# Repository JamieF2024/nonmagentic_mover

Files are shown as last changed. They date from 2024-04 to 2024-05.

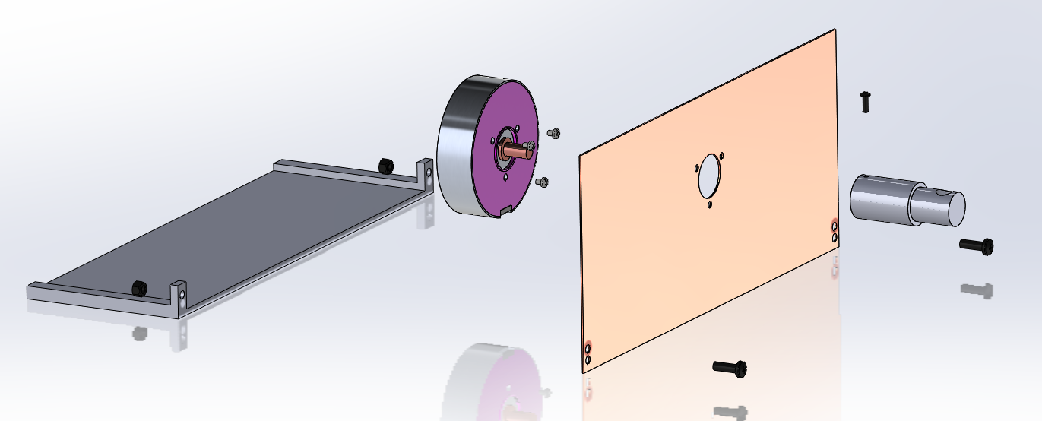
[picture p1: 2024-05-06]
SOLIDWORKS/Final Motor Assembly.png

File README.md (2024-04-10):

# nonmagentic_mover
<h1>MRI Compatible Motion Platform</h1>

Our team is working on developing an advanced MRI-compatible device that is capable of positioning a phantom and replicating physiological movements to enhance the accuracy of qMRI evaluations.

<h2>Project Overview</h2>
Imagine a clinic where doctors can quickly and painlessly measure characteristics of tissue inside a patient, without an invasive biopsy – this is the goal of quantitative magnetic resonance imaging (MRI).

Liver disease is a major public health challenge worldwide. Excessive fat accumulation (steatosis) in the liver affects approximately 25% of the world population (i.e., over one billion people), and prevalence is increasing everywhere. If untreated, steatosis can lead to further liver damage, cirrhosis, and cancer. Thus, it would be highly impactful to have a non-invasive measuring technique like quantitative MRI to determine clinically relevant quantities like liver fat and iron concentration. Making these MRI techniques robust against respiratory and other bodily motion is important for improving their “foolproofness” and facilitating their widespread adoption for use in a wider range of patients.

The Quantitative Imaging Methods Lab (QIML) in the Department of Medical Physics and Radiology is interested in the development of these motion-robust quantitative MRI methods. A motion platform which is safe for use in the highly magnetized environment of the MRI scanner, and can produce consistent motion patterns which mimic that of patients, would contribute greatly to the development and testing process for motion-robust MRI methods.

The development of a mechanical device which is MR-compatible poses some unique challenges. Magnetic metals must not be used at all, and the use of other metals (eg. brass, aluminum) should still be minimized due to the possibility of induced currents as the magnetic field varies over the course of operation of the MRI scanner. A nonmagnetic piezoelectric ultrasonic motor is available for students to integrate into their design, as well as nonmetallic linear sliding rails and bearings. Depending on the interests of the students, the project could be extended to creating motion with multiple degrees of freedom (2D planar motion or translational motion and compressive deformation) or the implementation of a MR-compatible form of closed-loop feedback.

<h2>Project Contributors </h2>
Team Members: Maxwell Naslund, Caspar Uy, Kendra Besser, Jamie Flogel, Amber Schneider 
<br></br>
Advisor: Dr. James Trevathan
<br></br>
Client: Mr. Jiayi Tang

<h2>Team Photo </h2>

Team Photo 

This project is affiliated with the University of Wisconsin-Madison, Department of Biomedical Engineering.

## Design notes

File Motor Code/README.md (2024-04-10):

<h1>Motor Code Overview</h1>
The motor assembly utilizes a WLG-75-R piezoelectric motor to generate rotational motion. This motor is controlled by a WLG-75-R-AMAG and Nucleo Board F446RE. The motor code is written in C++. It can be edited, uploaded, and run through <a href="https://studio.keil.arm.com/">Keil Studio Cloud - Arm</a>. Below are instructions for how to set up and run the main.cpp files in this folder.
<h2>Setup</h2>
<ol>
  <li>Login or Create an Account with Keil Studio Cloud.</li>
  <li>In the top right, go to File -> New -> Mbed Project.</li>
  <li>For the "Example project" field, select "empty Mbed OS project". Edit the project name to something memorable. The project should now appear as <b>active</b> in the left panel.</li>
  <li>Right click on the project name in the left panel and select Add Mbed Library.</li>
  <li> For the "URL" field, use <a href=http://os.mbed.com/users/aberk/code/QEI/>http://os.mbed.com/users/aberk/code/QEI/</a>. The Library Name field should auto-populate as "QEI". </li>
  <li>Click Next. For the "Release, Branch, or Tag" field, select "default". Click Finish. There should now be a subfolder labeled QEI. This folder contains 2 files: QEI.cpp & QEI.h.</li>
  <li>Replace the current QEI.cpp and QEI.h files in Keil Studio Cloud with the files in the GitHub Motor Code folder. You can do this by either downloading then uloading the files, or by copying and pasting their contents.</li>
  <li>Do the same for the main.cpp file found in Keil Studio Cloud and this GitHub folder.</li>
<i>Note: the main.cpp file is currently not uploaded in GitHub. Please use the Google Drive.</i>
</ol>
<b>You have now successfully finished the setup!</b>
<h2>Building & Running a Program</h2>
<i>When working in Keil Studio Cloud, make sure that the project you are working on is <b>active</b>.</i>
<ol>
  <li> Plug the Nucleo Board into the computer you are using with Keil Studio Cloud.</li>
  <li>Ensure your current project is <b>active</b>. Set the "Build target" in the left pane as "NUCLEO-F446RE".</li>
  <li>Build the project using the blue hammer button in the left pane. This will take around a minute the first time you build, but in future builds it will be quicker. Upon completion, a download should be completed as a ".bin" file.</li>
  <li> Open file explorer. Find the Nucleo Board connection under "This PC". Drag and drop the ".bin" file into the Nucleo drive.</li>
</ol>
<b>Your code is now successfully uploaded and running!</b>

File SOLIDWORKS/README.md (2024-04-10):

<h2>SOLIDWORKS Files</h2>
Many components of our design were 3D printed using PLA.
The final versions of the printed files are included in this folder.

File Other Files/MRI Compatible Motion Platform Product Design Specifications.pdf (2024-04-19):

## MRI Compatible Motion Platform - BME 400

Product Design Specifications February 27th, 2024

Client: | Mr. Jiayi Tang
Advisor: | Dr. James Trevathan
Team: | Maxwell Naslund - Team Leader Kendra Besser - Communicator Amber Schneider - BWIG Jamie Flogel - BPAG Caspar Uy - BSAC

Function

MRI phantoms are often static models of the human body that are used to test and calibrate MRI’s. Natural process’ such as respiration and digestion create constant motion within the human body. Static phantoms used to calibrate MRI’s do not properly represent this motion. This demonstrates a need for an MR compatible device that holds a phantom and is capable of simulating the movements found within the human body.

Client requirements:

- MR Compatible
- Moves back and forth
- Minimize the use of electronics inside the room
- Potentially incorporate materials currently available from the client
- Create a prototype with a budget of $1000
- Utilize commercially available parts
- Avoid complex fabrication methods

Design requirements:

### 1. Physical and Operational Characteristics

a. Performance requirements: The product will be a magnetic resonance compatible platform that provides a periodic waveform motion. The waveform motion will have a frequency of 4-20 cycles/min and amplitude of 1-6 cm to represent physiological breathing patterns. The motion will be consistent for 15 minutes and is allotted a standard deviation of 5% from the desired waveform. The product must withstand the size and weight of a phantom liver for testing purposes.
b. Safety: The device will be entirely made of MR compatible material and will pose no safety risk within the MR environment. The device’s magnetically induced displacement and torque forces will be tested to assure these forces are below their gravitational equivalents. The device will also be evaluated for RF heating, eddy currents, gradient induced vibrations, and gradient induced extrinsic electrical potential risks, as also recommended by the FDA [1]. As this device will utilize electronics, it is classified as an active medical device and will follow FDA 21 CFR part 801 and ASTM F2503 labeling requirements.
c. Accuracy and Reliability: The device must be able to produce repeatable patterns of movements within 2mm. The components of the device must not decrease the signal to noise ratio of the calibration phantom being tested. The device must be able to reliably repeat MR scans with minimal decrease in image quality between scans.
d. Life in Service: The device must operate for up to 60 minutes at a time as that is the time an MRI may take to produce an image of a medium-sized area [2]. A non-magnetic motor should last 20,000 hours under normal operating conditions [3]. Overall the device should last as long as an MRI scanner, which is approximately 10 years [4].
e. Shelf Life: Based on the motor components it should be stored in -40 to 70 °C temperatures with humidity 0 to 80% non condensing [2].
f. Operating Environment: The device must be able to withstand upwards of 3 tesla for 1 hour [5]. The device must be able to withstand potential RF heating, eddy currents, gradient induced vibrations, and gradient induced extrinsic electrical potential risks associated with devices within strong magnetic fields [1].
g. Ergonomics: The platform should have a height that is comfortable and safe for people to interact with when placed in the MRI. No force should be applied by a person to the motor or any moving parts during operation. An emergency stop feature should be implemented to allow users to immediately stop the motion platform in case of any issues or safety concerns.
h. Size: The platform will be no smaller than 25cm x 35cm in order to hold a range of phantom liver samples [6]. The platform will be rectangular shaped.
i. Weight: In order for the user to install and uninstall the platform during each segment of testing, the weight should not exceed 10kg. The platform must be able to withstand 4kg [7].

j. Materials: The product will be composed of MRI compatible materials. Ferrous and magnetic metals will not be used; other metals, such as brass and aluminum, will be limited to minimize the possibility of induced currents. A nonmagnetic ultrasonic piezoelectric motor will be used to provide platform motion. Nonmetalic sliding rails and bearings will be used to guide the platform through the MRI machine.
k. Aesthetics, Appearance, and Finish: Color, shape, form, texture of finish should be specified where possible (get opinions from as many sources as possible).

### 2. Production Characteristics

a. Quantity: Produce one motion controlled platform.
b. Target Product Cost: The budget for this project is $1000 with many of the components already provided including some motors, rails, software, and hardware. Existing MRI compatible designs cost around $9700 excluding the cost of the phantom used [7].

### 3. Miscellaneous

a. Standards and Specifications: MRI systems and accessories must follow the multiple sets of standards designed by the organizations like the FDA involving forms of testing the functionality of the machine including any additional accessories. Accessory parts should allow appropriate function in testing MRI displacement force ASTM F2052, torque ASTM F2213, RF heating ASTM F2182, and image artifact ASTM F2119 [8].
b. Customer: Preferences on stability and levelness will assist users in creating more genuine images. Reducing additional noise from both the platform and machine would be beneficial to more optimal usage.
c. Patient-related concerns: The device would need to be appropriately cleaned and disinfected for each use as instructed with the associated manufacturer. Appropriate dimensions levelness of the platform will need to be monitored to help with specimen/subject safety. Additionally cleanliness of the machine is an important consideration as the device should not leak motor oil or other fluids on the MRI bed.
d. Competition:
- Vital Biomedical Technologies MRI Compatible Multi-Modality Motion Stage is a programmable linear motion stage. This product is used in the bore of the MRI scanner and follows user-defined trajectories. The programmed trajectories are loaded onto the control system through a micro SD card. This product has a patent pending and there are a suite of other similar motion stages by this same company to address different anatomical motions [9].
- For a study done by the Department of Radiology at University of Texas Southwestern Medical Center researchers developed a one-dimensional MRI compatible motion platform. They used this in combination with an abdominal phantom to assess how movement during imaging affected the quality of images and the accuracy of quantitative metrics. This design consisted of a motorized linear stage residing inside the MRI machine and driving electronics outside the MRI room. The motorized stage followed sinusoidal, harmonic, random or user-defined trajectories. The device was used for the study and is not on the market for outside use [7].
- The Quasar MRI Motion Phantom is a completely MR safe programmable phantom. In this device the motion capable components are incorporated directly with the phantom. This design uses piezoelectric motors to create desired motions. It is intended to be used to test Deep Inspiration Breath Hold protocols. It is unclear how useful this product would be in protocols that require normal respiratory movement rather than breath holding [10].

## References

[1] “Testing and labeling medical devices for safety in the magnetic ...,” U.S. FOOD & DRUG ADMINISTRATION, https://www.fda.gov/media/74201/download?attachment (accessed Sep. 22, 2023).
[2] “How it’s performed - MRI Scan,” NHS choices, https://www.nhs.uk/conditions/mri-scan/what-happens/#:~:text=A%20magnetic%20reso nance%20imaging%20(MRI,number%20of%20images%20being%20taken. (accessed Sep. 20, 2023).
[3] “Hr4 nanomotion motor ,” NANOMOTION, https://www.nanomotion.com/product/hr4-nanomotion-motor/ (accessed Sep. 20, 2023).
[4] A. Sahu, H. Vikas, and N. Sharma, “Life cycle costing of MRI machine at a tertiary care teaching hospital,” The Indian journal of radiology &amp; imaging, https://www.ncbi.nlm.nih.gov/pmc/articles/PMC7546299/ (accessed Sep. 20, 2023).
[5] K. Albus, “Small phantom testing: MRI (revised 3-6-23),” Accreditation Support, https://accreditationsupport.acr.org/support/solutions/articles/11000061036-small-phant om-testing-mri-revised-3-6-23- (accessed Sep. 21, 2023).
[6] “Liver Phantom — The Phantom Laboratory.” https://www.phantomlab.com/liver-phantom (accessed Sep. 22, 2023).
[7] J. Nofiele et al., “An MRI-Compatible Platform for One-Dimensional Motion Management Studies in MRI,” Magnetic resonance in medicine, vol. 76, no. 2, p. 702, Aug. 2016, doi: 10.1002/mrm.25903. (https://doi.org/10.1002/mrm.25903)
[8] Center for Devices and Radiological Health. “MRI Information for Industry.” U.S. Food and Drug Administration, FDA, www.fda.gov/radiation-emitting-products/mri-magnetic-resonance-imaging/mri-informati on-industry. Accessed 20 Sept. 2023.
[9] “Motion Stages Compatible with CT, MRI, PET, SPECT & Ultrasound.” https://www.simutec.com/Products/motionstages.html (accessed Sep. 20, 2023).

[10] “QUASARTM MRI⁴D Motion Phantom,” Modus Medical Devices. https://modusqa.com/products/quasar-mri4d-motion-phantom/ (accessed Sep. 20, 2023).

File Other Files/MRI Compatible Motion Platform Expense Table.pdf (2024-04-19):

Item | Description | Manufacturer | Part Number | Date | QTY | Cost Each | Total | Link

Component 1 - Gearbox Prints

Ultimaker PLA (118 g) | 3D printed support for the driveshaft | Ultimaker | RAL-9005 | 11/17/2023 | 1 | $9.44 | $9.44 | N/A
Ultimaker PLA (126 g) | 3D printed gearbox extension pieces | Ultimaker | RAL-9005 | 2/27/2024 | 1 | $6.30 | $6.30 | N/A
Ultimaker PLA | 3D Printed Gears | Ultimaker | RAL-9005 | 3/7/2024 | 1 | $2.56 | $2.56 | N/A
Ultimaker PLA | 3D Printed Gearbox and motor stand | Ultimaker | RAL-9005 | 3/14/2024 | 1 | $19.60 | $19.60 | N/A

Component 2 - Linear Rails

Linear Rails

400 mm linear
rails | igus

CWS-06-30-4
00 | 11/13/2023 | 2 | $167.69 | $335.38 | Link (https://www.igus.com/articlerouter/?artnr=CWS-06-30-400&c=US&l=en&q_ettig=c3tYhltIigbyygX)

Component 3 - Linear Slides

Linear Slides

Slides to support
platform on linear
slides | igus

WWPL-06-30
-06 | 11/13/2023 | 2 | $18.25 | $36.50 | Link (https://www.igus.com/product?artNr=WWPL-06-30-06&q_ettig=c3tYhltIigbyygX&utm_medium=email)

Component 4 - Driveshaft

Driveshaft

Connection piece
between motor
and gearbox Grainger

H0400075PW
1000 | 11/16/2023 | 1 | $8.00 | $8.00 | Link (https://www.grainger.com/product/GF-PIPING-SYSTEMS-Pipe-PVC-5AFJ3)

Component 5 - Platform

Platform

1/4 black acrylic
sheet provided by
Makerspace MSC

MSC#
63391700 (no
part number
given similar
example) | 11/17/2023 | 1 | $20.00 | $20.00 | N/A

Component 6 - Glass Ball Bearings

Glass Ball Bearings

Glass ball
bearings to allow
for frictionless
rotation | Grainger | MSN0459939 | 12/1/2023 | 5 | $17.07 | $85.35 | N/A

Component 7 - Fastner

M5 Plastic Screws | Used to assemble final prototype | Grainger | 50M050080 H016 | 2/15/24 | 1 | $1.65 per package of 25 | $1.65 | Link (https://www.grainger.com/product/Machine-Screw-M5-Thread-Size-4DJK4)
M4 Plastic Screws | Used to assemble final prototype | Grainger | 50M040070N 035 | 2/15/24 | 2 | $5.92 per package of 25 | $11.84 | Link (https://www.grainger.com/product/Machine-Screw-M4-Thread-Size-4DFC2)

Plastic Screws and
Nuts

Plastic hardware
from the
makerspace | Makerspace | N/A | 3/6/2024 | 1 | $1.30 | $1.30 | N/A

Component 8 Power Components

Power Inverter

Power supply
inverter to
improve circuit DigiKey

PDM1-S5-D3
-S | 3/22/2024 | 2 | $5.12 | $10.24 | Link (https://www.digikey.com/en/products/detail/cui-inc/PDM1-S5-D3-S/5306611?_gl=1*1pgc32a*_up*MQ..)

Component 9 - unused features due to reprints/redesigns

Ultimaker PLA | 3D printed Gearbox | Ultimaker | RAL-9005 | 10/26/202 3 | 1 | $19.36 | $19.36 | N/A
Ultimaker PLA | Motor to driveshaft adapter piece | Ultimaker | RAL-9005 | 12/1/2023 | 1 | $1.12 | $1.12 | N/A
Ultimaker PLA | Motor to driveshaft adapter piece reprint | Ultimaker | RAL-9005 | 12/4/2023 | 1 | $2.84 | $2.84 | N/A
Ultimaker PLA | Motor to driveshaft adapter piece reprint | Ultimaker | RAL-9005 | 12/5/2024 | 1 | $2.65 | $2.65 | N/A
Ultimaker PLA (37.0 g) | 3D printed gears to translate and facilitate motion | Ultimaker | RAL-9010 | 10/26/202 3 | 1 | $2.96 | $2.96 | N/A

Ultimaker PLA (325.0 g) | 3D printed gears and gearbox | Ultimaker | RAL-9005 | 11/03/2023 | 1 | $26.00 | $26.00 | N/A
Bamboo Labs PLA (127.34 g) | 3D printed gearbox extension pieces | Bambu Lab | #000000 | 11/15/2023 | 1 | $12.19 | $12.19 | N/A
Ultimaker PLA (27 g) | 3D printed racks | Ultimaker | RAL-9005 | 11/29/2023 | 1 | $2.16 | $2.16 | N/A
Ultimaker PLA (126 g) | 3D printed Motor Stand | Ultimaker | RAL-9005 | 12/01/202 3 | 1 | $10.08 | $10.08 | N/A
Ultimaker PLA | 3D printed gears and gearbox | Ultimaker | RAL-9005 | 2/23/24 | 1 | $14.60 | $14.60 | N/A
TOTAL: | $642.12

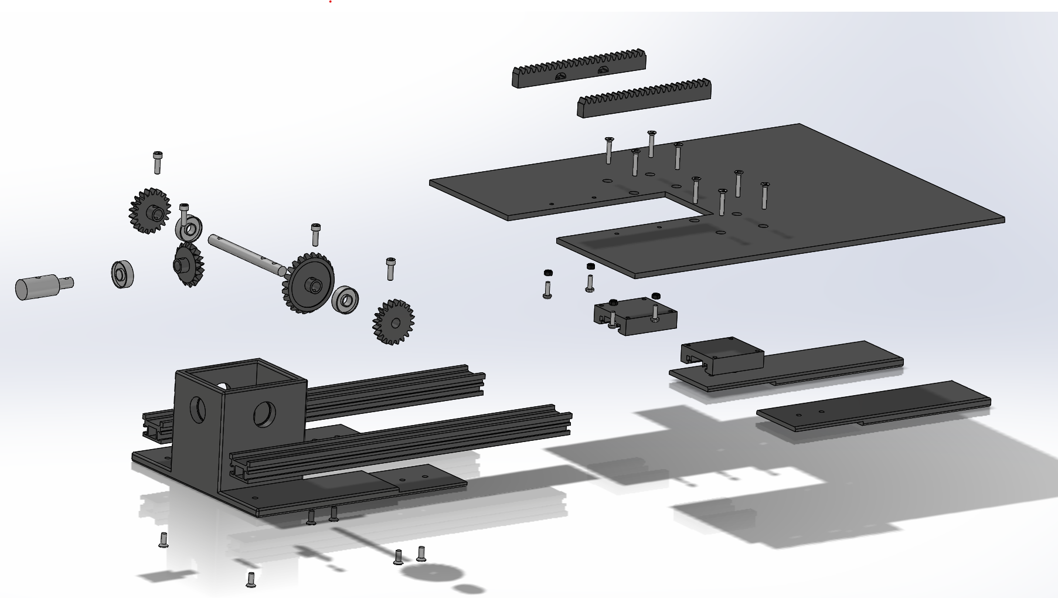
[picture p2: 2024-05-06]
SOLIDWORKS/final exploded.png

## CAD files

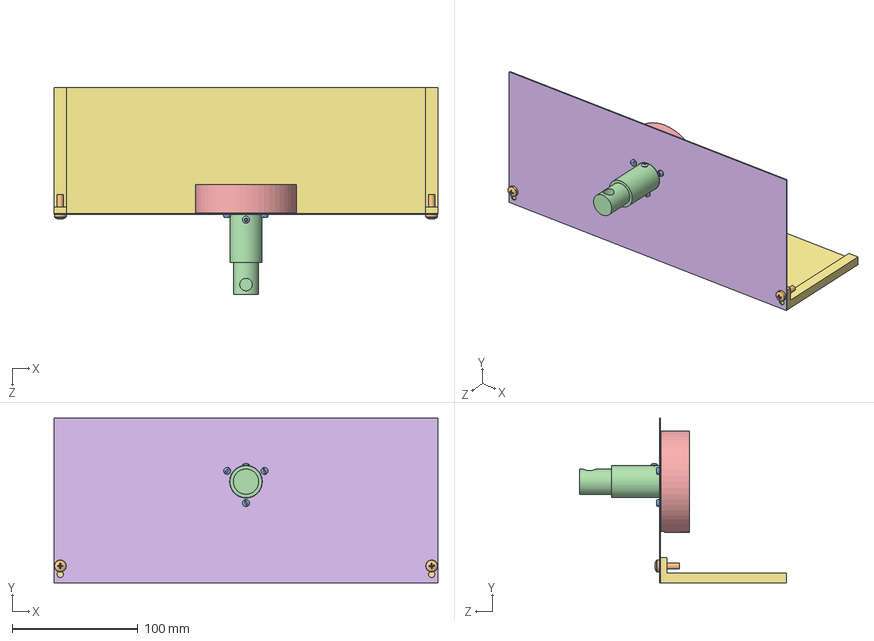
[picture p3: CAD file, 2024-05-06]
SOLIDWORKS/Final Motor Assembly.SLDASM
304.8 x 130.6 x 164.5 mm
MotorStand
MotorCopperFace
Motor
MotorDriveshaft Adaptor
Motor_M3 x 3
Stand_M5 x 2
Adaptor_M3

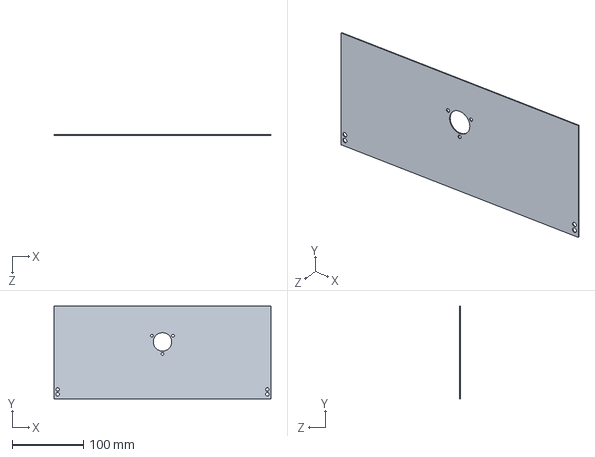
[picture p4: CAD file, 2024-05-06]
SOLIDWORKS/MotorCopperFace.SLDPRT
304.8 x 130.6 x 1.00 mm

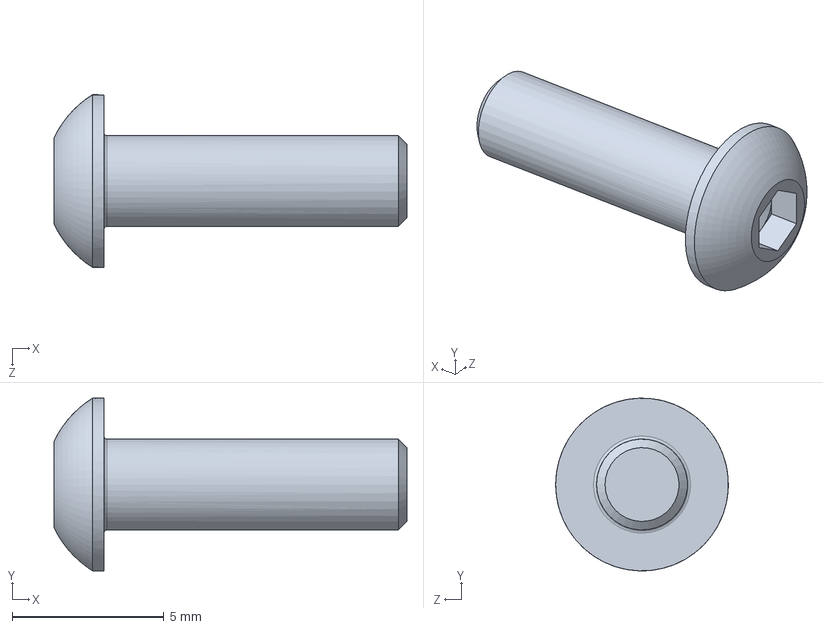
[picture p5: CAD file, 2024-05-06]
SOLIDWORKS/Adaptor_M3.SLDPRT
11.6 x 5.70 x 5.70 mm

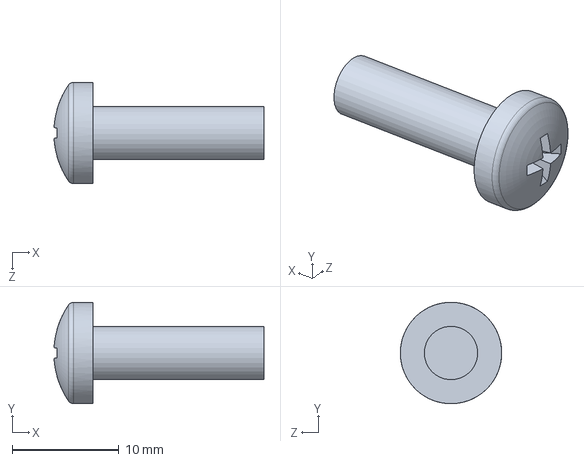
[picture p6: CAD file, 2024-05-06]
SOLIDWORKS/Stand_M5.SLDPRT
19.7 x 9.50 x 9.49 mm

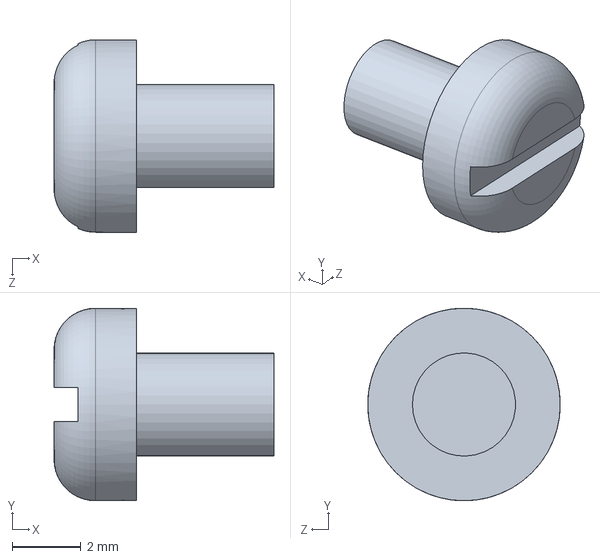
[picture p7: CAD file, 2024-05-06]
SOLIDWORKS/Motor_M3.SLDPRT
6.40 x 5.60 x 5.60 mm

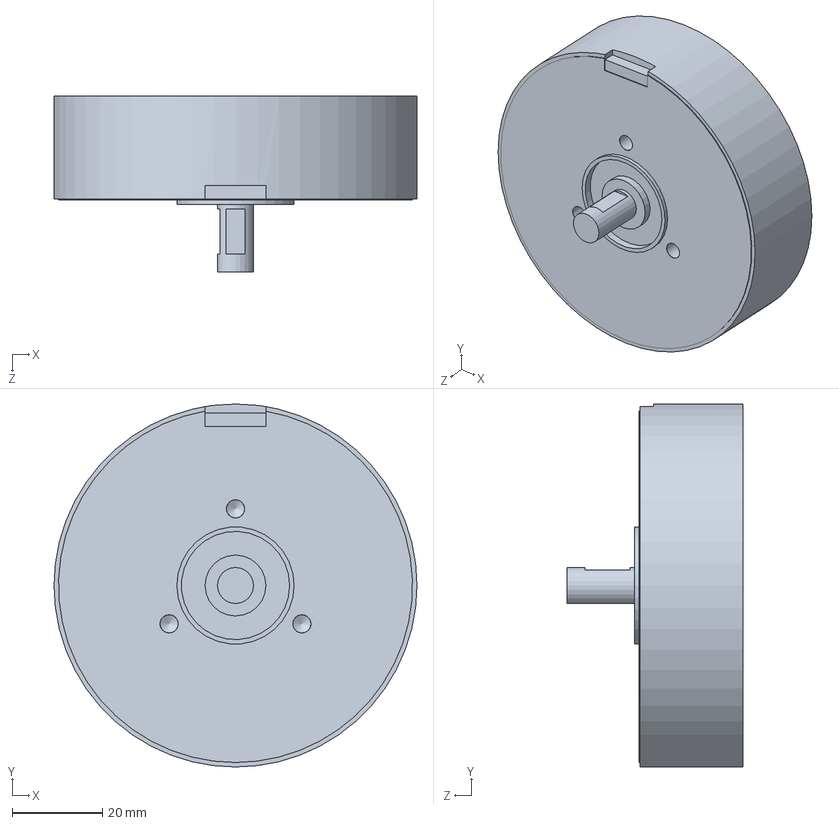
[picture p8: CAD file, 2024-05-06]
SOLIDWORKS/Motor.SLDPRT
80.5 x 80.5 x 39.0 mm

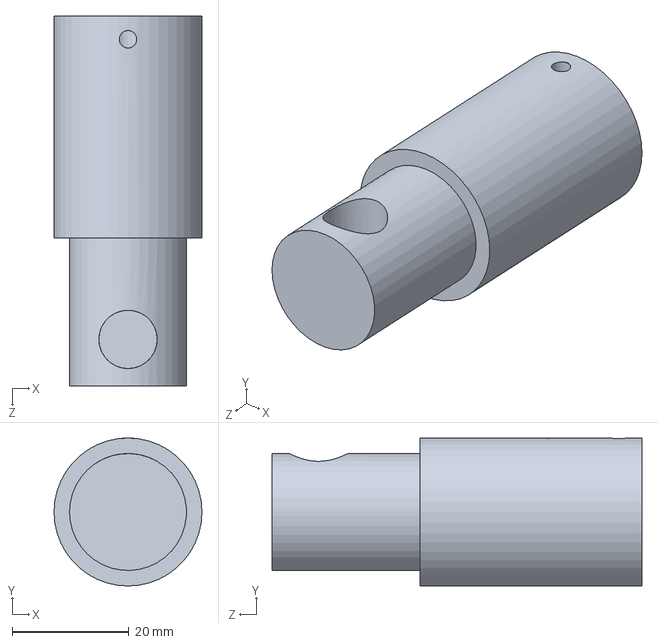
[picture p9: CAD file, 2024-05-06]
SOLIDWORKS/MotorDriveshaft Adaptor.SLDPRT
25.4 x 25.4 x 63.5 mm

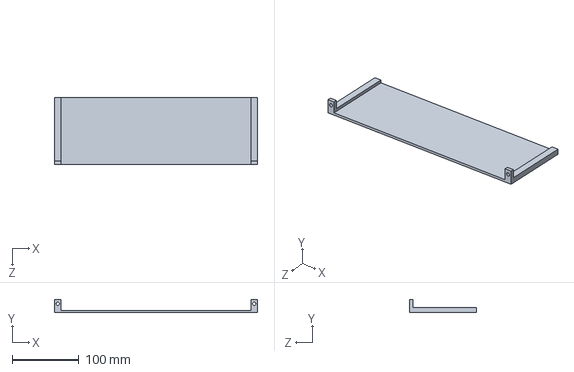
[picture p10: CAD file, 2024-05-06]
SOLIDWORKS/MotorStand.SLDPRT
304.8 x 20.0 x 100.0 mm

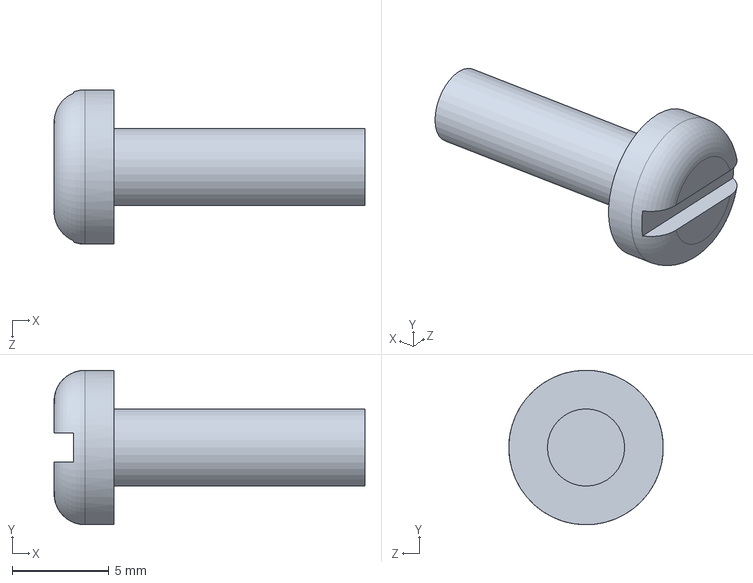
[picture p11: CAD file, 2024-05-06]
SOLIDWORKS/Rack_M4.SLDPRT
16.1 x 8.00 x 8.00 mm

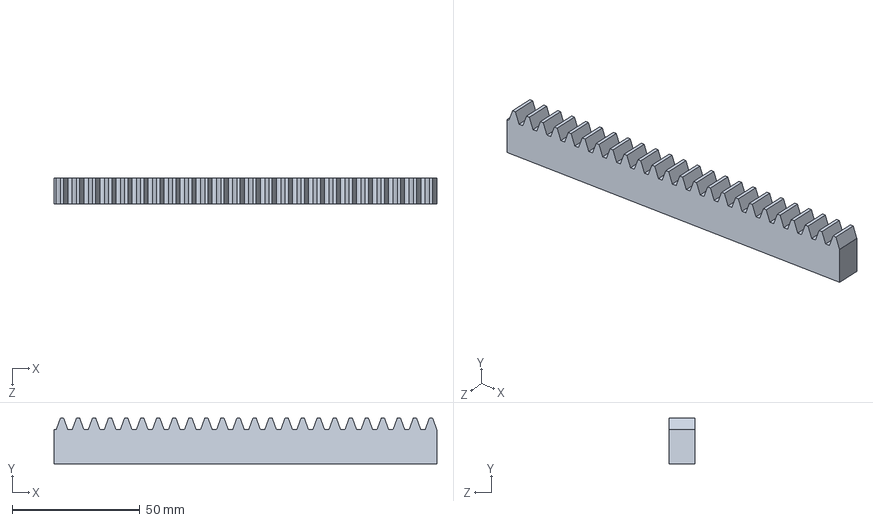
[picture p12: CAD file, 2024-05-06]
SOLIDWORKS/Rack.SLDPRT
150.0 x 18.0 x 10.0 mm

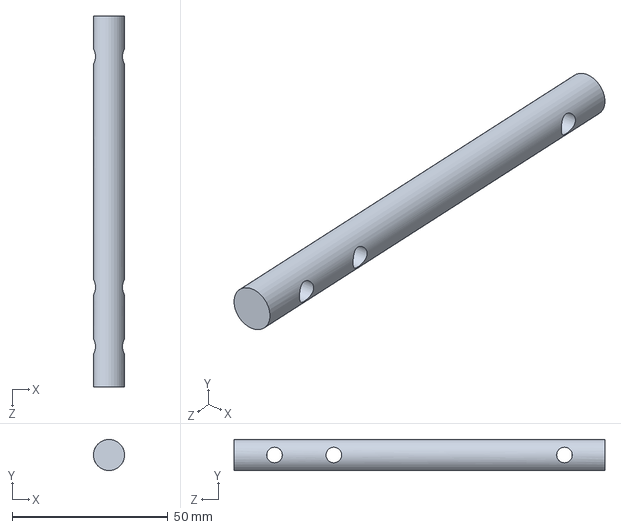
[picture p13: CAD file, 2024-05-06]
SOLIDWORKS/crosspin_new.SLDPRT
9.99 x 9.98 x 119.0 mm

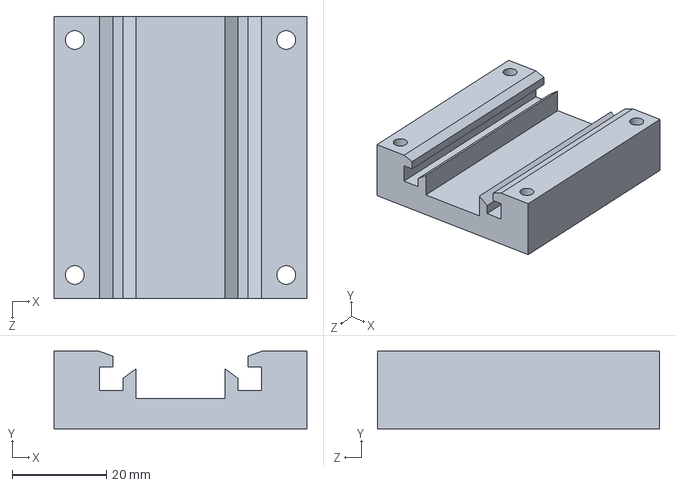
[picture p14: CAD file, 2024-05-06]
SOLIDWORKS/slide.SLDPRT
53.8 x 16.5 x 60.0 mm

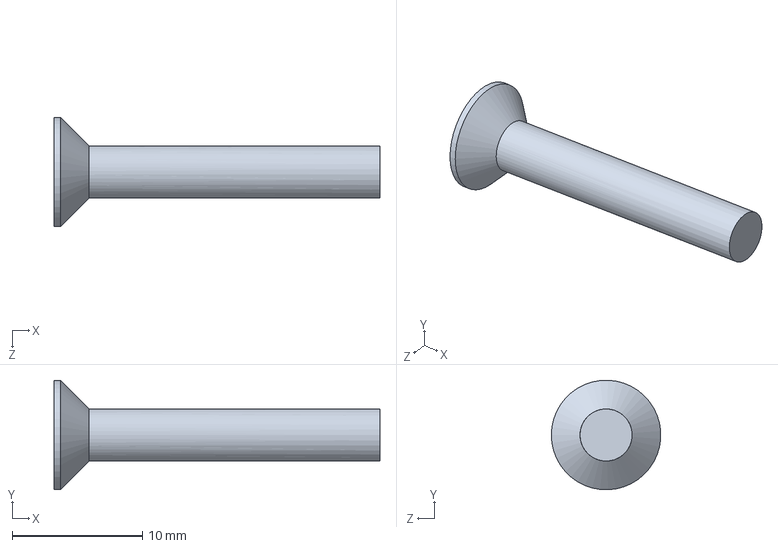
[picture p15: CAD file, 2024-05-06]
SOLIDWORKS/Slide_M4.SLDPRT
25.0 x 8.39 x 8.39 mm

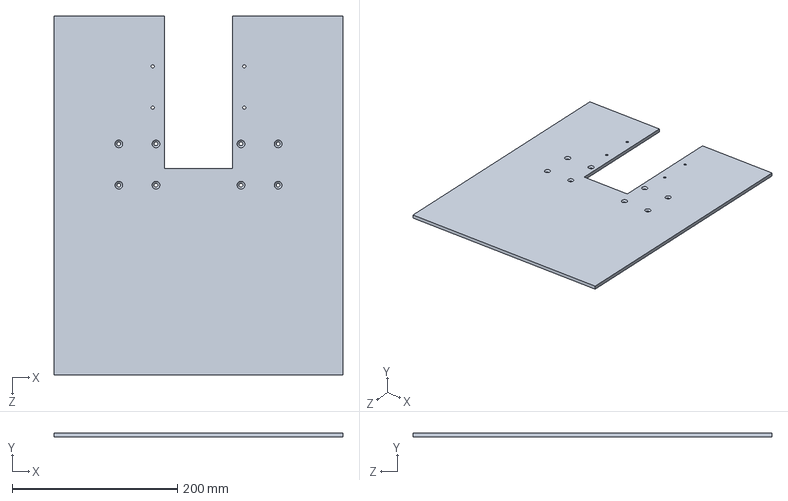
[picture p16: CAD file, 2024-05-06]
SOLIDWORKS/NewPlatform.SLDPRT
350.0 x 5.30 x 435.0 mm

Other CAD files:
SOLIDWORKS/Final Assembly.SLDASM
SOLIDWORKS/3D Printed Components.SLDASM
SOLIDWORKS/extension.SLDPRT
SOLIDWORKS/spring_gearbox.SLDPRT
SOLIDWORKS/1-1_BevelGear.SLDPRT
SOLIDWORKS/1.5-1_BevelGear.SLDPRT
SOLIDWORKS/BallBearing.SLDPRT
SOLIDWORKS/Driveshaft pin new.SLDPRT
SOLIDWORKS/Gear_M5.SLDPRT
SOLIDWORKS/Gears_M5.SLDPRT
SOLIDWORKS/M4_Nut.SLDPRT
SOLIDWORKS/MotorStand.STL
SOLIDWORKS/Rail_M5.SLDPRT
SOLIDWORKS/Stand_M5_Nut.SLDPRT
SOLIDWORKS/metric_gear.SLDPRT
SOLIDWORKS/rail.SLDPRT

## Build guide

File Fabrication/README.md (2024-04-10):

<h2>Fabrication Information</h2>
We utilized the TEAMLab at the University of Wisconsin-Madison to fabricate much of our design. This folder outlines our fabrication process.

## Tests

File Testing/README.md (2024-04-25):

<h1>Testing and Validation Information</h1>

<h2>First Round of Testing</h2>
3 tests were performed: motor encoder test, motor RPM test, and platform sinusoidal motion test.

<h3>Motor Encoder Test</h3>
This test is performed to determine if the number of revolutions counted by the motor encoder is accurate. It will reveal if there is any error associated with the built in encoder. This is important to determine its accuracy before relying on encoder values for motor control in the overall device. Additionally, it is important to validate the capabilities of the motor since it is MR compatible. For a full testing protocol refer to Testing Protocols Folder. This test is performed on the motor only, disconnected from the prototype. To perform this test, place a thin flag on the motor shaft to mark initial position. Run “revolutionsCounter()” on Mbed by pressing 4. This program will rotate the motor at 60 RPM until the encoder counts 60 revolutions. During the test, visually count the number of rotations. Make note if the motor's final position is different from its starting position. The motor is expected to stop after 60 full revolutions in the same position as it started. If the motor spins more or less than 60 revolutions during the test, then there is some error associated with the encoder values that needs to be addressed.

<h3>Motor RPM Test</h3>
This test is performed to determine if the rotations per minute of the motor is accurate. At programmed speeds the prototype will be assessed on how accurate the physical speed is compared to the expected speed. It will reveal if there is any error associated with the code to convert RPM to voltage to control the motor speed. This is important to determine the accuracy of the speed since the prototype’s sinusoidal motion is dependent on this conversion. For a full testing protocol refer to the Testing Protocols Folder. This test is performed on the motor only, disconnected from the prototype. To perform this test, place a thin flag on the motor shaft to mark initial position. Begin recording a video in full view of the motor from above. Run “motorRPMTest()” on Mbed by pressing 5. This program will rotate the motor at a predetermined RPM (20, 40, or 60) until the encoder counts 1 revolution. Once complete, stop the recording. Measure the time it took to spin 1 revolution. The equation of the experimental RPM is 60/experiment_time. If the motor spins more or less than the expected RPM during the test, then there is some error associated with the RPM to voltage conversion that needs to be addressed.

<h3>Platform Sinusoidal Motion Test</h3>
This test is performed to determine if the platform is moving at the expected displacement of the sine wave. Trials will be conducted at different weights, but the motor velocity will be constant throughout trials. The prototype will be assessed on how accurate the displacement is over the course of the test in comparison to expected displacement. The expected displacement is calculated by taking the integral of the motor velocity with respect to time. Motor Velocity = A×sin(2π×f×t), with A=10 RPM and f = 8/60 cycles per second therefore, Expected Displacement = A/(2π×f×t)×cos(2π×f×t). This is important to determine if the accuracy of the sinusoidal motion is within 5% deviation. For a full testing protocol refer to Testing Protocols Folder. This test is performed on the entire prototype assembly. To perform this test, place a bright marker on the platform to mark the initial position. Begin recording a video in full view of the platform from above. Run “sinusoidalSpeedVariation()” on Mbed by pressing 2. This program will set the velocity of the motor to a sine wave that varies over time for 60 seconds. Once complete, stop the recording. Measure the displacement throughout the entire time the motor is moving. Identifying key aspects of the wave and comparing them to the expected wave will determine if the sinusoidal motion is within specifications, or if its accuracy needs to be improved.

<h2>Second Round of Testing</h2>
After making modifications to the protoype and software after preliminary testing we performed another round of testing. In this testing we performed variations of the Platform Sinusoidal Motion Test described above.

<h3>Weight Test</h3>
We performed the Platform Sinusiodal Motion Test as described above again to see if our device had made any improvements in accuracy. For results of this test look in the Test Results folder at the Kinovea Data Analysis Excel file. Based on the results of this test we recalibrated the RPM to voltage conversion factor experimentally and reran the trials for 0 kg and 1.5 kg.

<h3>Frequency and Amplitude Testing</h3>
We performed more Sinusoidal Motion Tests while keeping the weigth at 0 kg but varying the period and amplitude. We performed 3 trials for each amplitude and frequency variation. We tested out 1 cm and 6 cm amplitudes at a frequency of 8 cycles per minute to compare to our baseline 0 kg test. We also tested out 4 cycles per minute and 20 cycles per minute at an amplitude of 3.6 cm to compare to our baseline 0 kg test. In our inital testing there was an issue with the setup of the recording device so we reran all of the tests. During the 1 cm trial there was significant play between the gears and a disconnect between the driveshaft and the motor. This led us to get only 1 valid trial for the 1 cm test. Due to limited time we were unable to retest. Results of the test are included in the Test Results folder.

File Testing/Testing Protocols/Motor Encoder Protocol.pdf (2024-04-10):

# Motor Encoder Test

## Description:

This test is performed to determine if the number of revolutions counted by the motor encoder is accurate.

## Materials:

1. Ultrasonic Motor
2. Microcontroller & Wires
3. Post-It flag
4. Stopwatch

## Procedure:

1. Connect the motor to the microcontroller and plug into power.
2. Connect the microcontroller to a laptop with the required files.
3. Ensure that the latest version of the active program is uploaded to the motor.
a. The latest main.cpp can be downloaded from Lab Archives.
4. Place a thin post-it flag on the motor shaft to mark an initial position.
5. Run the function “revolutionsCounter()” by pressing 4 and start a stopwatch at the same time.
a. This program will rotate the motor at 60 RPM until the encoder counts 60 revolutions.
b. This program is expected to run for 60 seconds.
6. While the program is running, visually count the actual number of revolutions.
7. Compare actual number of revolutions against expected value. Make a note if the motor does not end in the same orientation as it started.
8. Repeat 3-5 times.

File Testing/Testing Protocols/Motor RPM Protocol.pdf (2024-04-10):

# Motor RPM Test

## Description:

This test is performed to determine if the rotations per minute of the motor is accurate. At programmed speeds the prototype will be assessed to how accurate the physical speed is compared to the expected speed. At least 5 trials will be conducted for each set speed. The load will be constant throughout the trials.

## Materials:

1. Ultrasonic Motor
2. Microcontroller & Wires
3. Post-It flag
4. Camera
5. Kinovea software

## Procedure:

1. Connect the motor to the microcontroller and plug into power.
2. Connect the microcontroller to a laptop with the required files.
3. Ensure that the latest version of the active program is uploaded to the motor.
a. The latest main.cpp can be downloaded from Lab Archives.
4. Place a thin post-it flag on the motor shaft to mark an initial position.
5. Set-up camera in full view of the platform and begin recording a video.
6. Run the function “motorRPMTest()” by pressing 5.
a. This program will rotate the motor at 20 RPM until the encoder counts 1 revolution.
7. Once complete, stop recording the video.
8. Compare the time to complete the rotation to the expected time.
9. Repeat steps 4-8 until 5 or more trials are completed.
10. Repeat the procedure for a speed of 40 RPM and 60 RPM.

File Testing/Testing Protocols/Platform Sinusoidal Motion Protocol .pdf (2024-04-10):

# Platform Sinusoidal Motion Test

## Description:

This test is performed to determine if the platform is moving at the expected displacement of the sine wave. Multiple trials will be conducted at different weights. The motor velocity will be constant throughout trials.

## Materials:

1. Fully assembled prototype
2. Bright marker
3. Camera
4. Kinovea software

## Procedure:

1. Assemble complete prototype.
2. Connect the motor to the microcontroller and plug into power.
3. Connect the microcontroller to a laptop with the required files.
4. Ensure that the latest version of the active program is uploaded to the motor.
a. The latest main.cpp can be downloaded from Lab Archives.
5. Place a bright marker on the platform to mark the initial position.
6. Set-up camera in full view of the platform and begin recording a video from the top view.
7. Run the function “sinusoidalSpeedVariation()” by pressing 2.
a. This program will set the velocity of the motor to a sine wave with amplitude of 10 RPM, frequency of 8/60 Hz, and offset of 0. It will for 60 seconds
8. Once complete, stop recording the video.
9. Upload the video to Kinovea. Calibrate by drawing a line of known length on the video.
10. Place a tracking marker on the bright dot in the video. Track the displacement throughout the entire time the platform is moving.
11. Export the data to excel to perform statistical analysis.
12. Repeat steps 5-11 with different weights on the platform, ranging from 0-4 kg.

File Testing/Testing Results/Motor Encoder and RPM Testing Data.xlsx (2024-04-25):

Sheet: Scrap
set hexavelocity | revolutions | cacluated speed | test rotation: | mean: | test rotation: | mean:
0.1 | 10 | 32.14 | 3.19 | 3.337 | 5.13 | 5.06
 |  |  | 3.35 |  | 4.93
 |  |  | 3.34 |  | 5.13
 |  |  | 3.37 |  | 5
 |  |  | 3.32 |  | 5.13
 |  |  | 3.43 |  | 5.07
 |  |  | 3.38 |  | 5.03
 |  |  | 3.19
 |  |  | 3.5
 |  |  | 3.3
0.01 | 10

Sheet: Motor Encoder Test
motor should run for 60 sec at 60 rmp
trial # | counted rotations (code output) | counted rotations (visually) | time the motor ran for
1 | 60 | 60 | 53.39
2 | 60 | 60 | 52.7
3 | 60 | 60 | 53.6
4 | 60 | 60 | 52.9
5 | 60 | 60 | 53.64
Average | 60 | 60 | 53.25 | 0.42
Difference | 0

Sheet: Preliminary Motor RPM Test
motor should run for 60 sec at 60 rmp
trial # | Revolutions (code output) | Duration (sec)
1 | 60 | 53.39
2 | 60 | 52.7
3 | 60 | 53.6
4 | 60 | 52.9
5 | 60 | 53.64
Average | 60 | 53.25
Difference | 6.754
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

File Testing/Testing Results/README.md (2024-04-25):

<h3>Testing Results</h3>
This folder contains the testing data and results.

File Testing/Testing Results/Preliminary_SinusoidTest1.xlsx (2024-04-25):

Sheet: SinusoidTest1
x | y | t | time (s) | Observed | Calculated | Track
-10.65 | -13.83 | 5.5 | 5.5 | 2.705 | 2.705 | Label : | Trajectory 1
-10.65 | -13.83 | 5.54 | 5.54 | 2.705 | 2.703481364 | Coords (x,y:cm; t:time)
-10.75 | -13.82 | 5.57 | 5.57 | 2.605 | 2.700350073
-10.75 | -13.82 | 5.6 | 5.6 | 2.605 | 2.695513184
-10.75 | -13.82 | 5.64 | 5.64 | 2.605 | 2.68641628
-10.75 | -13.82 | 5.67 | 5.67 | 2.605 | 2.677613399
-10.85 | -13.82 | 5.7 | 5.7 | 2.505 | 2.66711928
-10.85 | -13.82 | 5.74 | 5.74 | 2.505 | 2.650507917
-10.85 | -13.82 | 5.77 | 5.77 | 2.505 | 2.636095191
-10.85 | -13.82 | 5.8 | 5.8 | 2.505 | 2.620017451
-10.85 | -13.82 | 5.84 | 5.84 | 2.505 | 2.596008145
-10.95 | -13.81 | 5.87 | 5.87 | 2.405 | 2.576086669
-10.95 | -13.81 | 5.9 | 5.9 | 2.405 | 2.554538081
-11.04 | -13.81 | 5.94 | 5.94 | 2.315 | 2.523299241
-11.04 | -13.81 | 5.97 | 5.97 | 2.315 | 2.49800875
-11.14 | -13.81 | 6 | 6 | 2.215 | 2.471140463
-11.14 | -13.81 | 6.04 | 6.04 | 2.215 | 2.432891205
-11.24 | -13.8 | 6.07 | 6.07 | 2.115 | 2.402409094
-11.34 | -13.8 | 6.1 | 6.1 | 2.015 | 2.37040957
-11.34 | -13.8 | 6.14 | 6.14 | 2.015 | 2.325418187
-11.44 | -13.8 | 6.17 | 6.17 | 1.915 | 2.289958265
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

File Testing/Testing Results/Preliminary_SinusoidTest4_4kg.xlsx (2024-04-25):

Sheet: SinusoidTest4_4kg
x | y | t | time (s) | Observed | Calculated
14.63 | -0.96 | 3.5 | 3.5 | 2.705 | 2.705 | Track
14.63 | -0.96 | 3.53 | 3.53 | 2.705 | 2.704145732 | Label : | Trajectory 1
14.83 | -0.95 | 3.57 | 3.57 | 2.505 | 2.700350073 | Coords (x,y:cm; t:time)
14.93 | -0.94 | 3.6 | 3.6 | 2.405 | 2.695513184
15.03 | -0.84 | 3.63 | 3.63 | 2.305 | 2.688973751
15.03 | -0.84 | 3.67 | 3.67 | 2.305 | 2.677613399
15.04 | -0.84 | 3.7 | 3.7 | 2.295 | 2.66711928
15.24 | -0.83 | 3.73 | 3.73 | 2.095 | 2.654940552
15.24 | -0.84 | 3.77 | 3.77 | 2.095 | 2.636095191
15.34 | -0.84 | 3.8 | 3.8 | 1.995 | 2.620017451
15.44 | -0.83 | 3.83 | 3.83 | 1.895 | 2.602284852
15.45 | -0.84 | 3.87 | 3.87 | 1.885 | 2.576086669
15.64 | -0.83 | 3.9 | 3.9 | 1.695 | 2.554538081
15.65 | -0.83 | 3.93 | 3.93 | 1.685 | 2.531375993
15.75 | -0.83 | 3.97 | 3.97 | 1.585 | 2.49800875
15.85 | -0.83 | 4 | 4 | 1.485 | 2.471140463
15.86 | -0.93 | 4.03 | 4.03 | 1.475 | 2.442711351
16.06 | -0.92 | 4.07 | 4.07 | 1.275 | 2.402409094
16.06 | -0.92 | 4.1 | 4.1 | 1.275 | 2.37040957
16.27 | -1 | 4.13 | 4.13 | 1.065 | 2.336912844
16.26 | -0.91 | 4.17 | 4.17 | 1.075 | 2.289958265
16.27 | -1 | 4.2 | 4.2 | 1.065 | 2.253051956
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

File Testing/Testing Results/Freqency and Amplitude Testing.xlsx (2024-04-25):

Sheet: Conclusions
 | Average Period (s) | Period Stdev | Average P-P | P-P Stdev | Percent error period | Percent error amplitude
Baseline (8/60, 3.6 cm) | 7.50 | 0.588 | 3.78 | 0.048 | 0.06 | 4.83
1 cm Amplitude | 7.53 | 0.574 | 1.29 | 0.065 | 0.42 | 29.19
6 cm Amplitude | 7.46 | 0.281 | 7.77 | 0.252 | 0.55 | 29.58
Low Frequency (4/60) | 15.03 | 0.634 | 4.64 | 0.194 | 0.21 | 28.65
High Frequency (20/60) | 3.01 | 0.177 | 4.64 | 0.114 | 0.32 | 28.67
4 cpm Redo | 15.07 | 0.682 | 4.11 | 0.101 | 0.45 | 12.06
6 cm Amplitude Redo | 7.56 | 0.552 | 6.48 | 0.231 | 0.81 | 6.16
20 cpm Redo | 3.02 | 0.184 | 3.94 | 0.036 | 0.51 | 7.35
1 cm Amplitude Redo (one trial only) | 7.437 | 0.843 | 0.736 | 0.042 | 0.84 | 27.63
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

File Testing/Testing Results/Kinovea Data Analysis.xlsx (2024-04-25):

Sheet: T1 0kg
Time(s) | Observed (cm) | Calculated (cm) |  | Period (s) | P-P Amplitude (cm)
3.84 | 2.03666667 | 1.79820988
7.91 | -1.6933333 | -1.6979973 |  |  | 3.72999997
11.77 | 1.98666667 | 1.63490671 |  | 7.93 | 3.67999997
15.28 | -1.7333333 | -1.753947 |  | 7.37 | 3.71999997
18.38 | 2.02666667 | 1.71739111 |  | 6.61 | 3.75999997
22.98 | -1.6533333 | -1.6594848 |  | 7.7 | 3.67999997
25.98 | 2.01666667 | 1.75739679 |  | 7.6 | 3.66999997
29.58 | -1.7033333 | -1.6928501 |  | 6.6 | 3.71999997
33.08 | 2.02666667 | 1.52663884 |  | 7.1 | 3.72999997
37.95 | -1.7333333 | -1.6766969 |  | 8.37 | 3.75999997
41.32 | 2.01666667 | 1.80023338 |  | 8.24 | 3.74999997
45.56 | -1.6933333 | -1.6084929 |  | 7.61 | 3.70999997
48.56 | 2.01666667 | 1.78053657 |  | 7.24 | 3.70999997
53.06 | -1.6933333 | -1.6084929 |  | 7.5 | 3.70999997
55.89 | 2.02666667 | 1.72193906 |  | 7.33 | 3.71999997
 |  |  | Average | 7.477 | 3.718
 |  |  | St Dev | 0.534 | 0.028
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
